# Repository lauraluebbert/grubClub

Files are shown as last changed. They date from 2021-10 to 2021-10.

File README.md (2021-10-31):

# grubClub
Please cite the information in this repository using the following DOI:  


I would like to present grubClub (“grub” for larva, and “club” for… well, you will see). I built off of the ethoscope (https://github.com/gilestrolab/ethoscope) by https://github.com/qgeissmann to enable automated long-term optogenetic stimulation of Drosophila larvae. Here is my Halloween-style release: https://twitter.com/NeuroLuebbert/status/1454220954666631170?s=20

GrubClub consists of a printed circuit board (PCB) and an accompanying arena. Both fit into the ethoscope published here: https://journals.plos.org/plosbiology/article?id=10.1371/journal.pbio.2003026.

The PCB holds 4 transistors, each connecting to 2 LEDs. Each row of LEDs can be controlled independently through Raspberry Pi GPIOs. In the picture below, each LED has a 270 ohm resistor. The power of the LEDs can be increased (or decreased) by modifying this resistance (within the circuit limits). 

The grubClub arena slides into the ethoscope and holds larvae in small round wells that can be filled with sugar-containing agar (or any larva medium). Each square fits a standard 22x22 mm coverslip as a lid. I 3D-printed my arena using translucent PLA to increase light intensity.

Since I am currently not recording larval behavior, I did not include an IR backlight for camera recordings. However, the PCB is designed such that an IR light strip can easily fit between the LED rows, enabling optogenetic stimulation and behavior recording at the same time. Finally, while red LEDs (~630 nm) might prevent a startle response, for my experimental design, I decided to stimulate at the spectral peak of my channelrhodopsin Chrimson (590 nm). The PCB supports LEDs of any color, and I included both options in the component list.

<p float="left">
  
   
</p>

<p float="left">
  
   
</p>

[grubClub PCB](https://user-images.githubusercontent.com/56094636/139601286-2ef72724-cccf-4f6b-9c9d-bd818d46505a.mp4)

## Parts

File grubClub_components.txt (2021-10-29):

2N3904 transistor:  
https://www.digikey.com/en/products/detail/nte-electronics-inc/2N3904/11648305

Yellow LEDs:  
https://www.digikey.com/en/products/detail/lumileds/LXM2-PL01-0000/3961250?s=N4IgjCBcoCwAxVAYygMwIYBsDOBTANCAPZQDaIATDAOwDMcArCIVXQGwQC6hADgC5QQAZT4AnAJYA7AOYgAvoQC0MRCBSQMOAsTIhaADgoBONiE4KQiiqvViArtpKRyRs3IvXnIUbgBGuTAACTDsAD1wiSTcgA

Red LEDs:  
https://www.digikey.com/en/products/detail/lumileds/LXM2-PD01-0050/3961247

PCB machined by https://oshpark.com/.

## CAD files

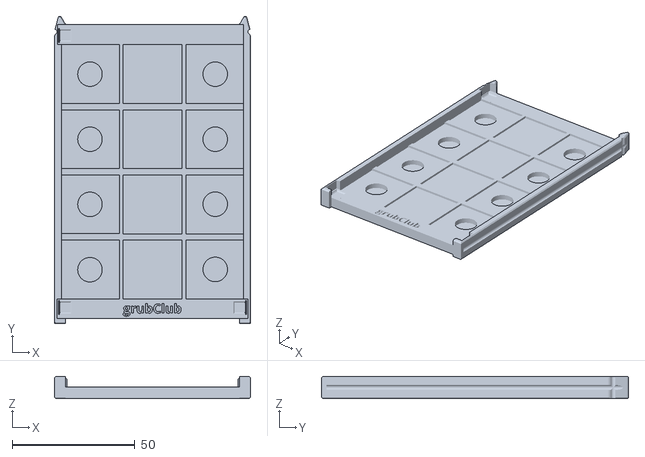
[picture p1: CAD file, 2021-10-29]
grubClub_arena_v2.stl
80.0 x 125.2 x 9.00

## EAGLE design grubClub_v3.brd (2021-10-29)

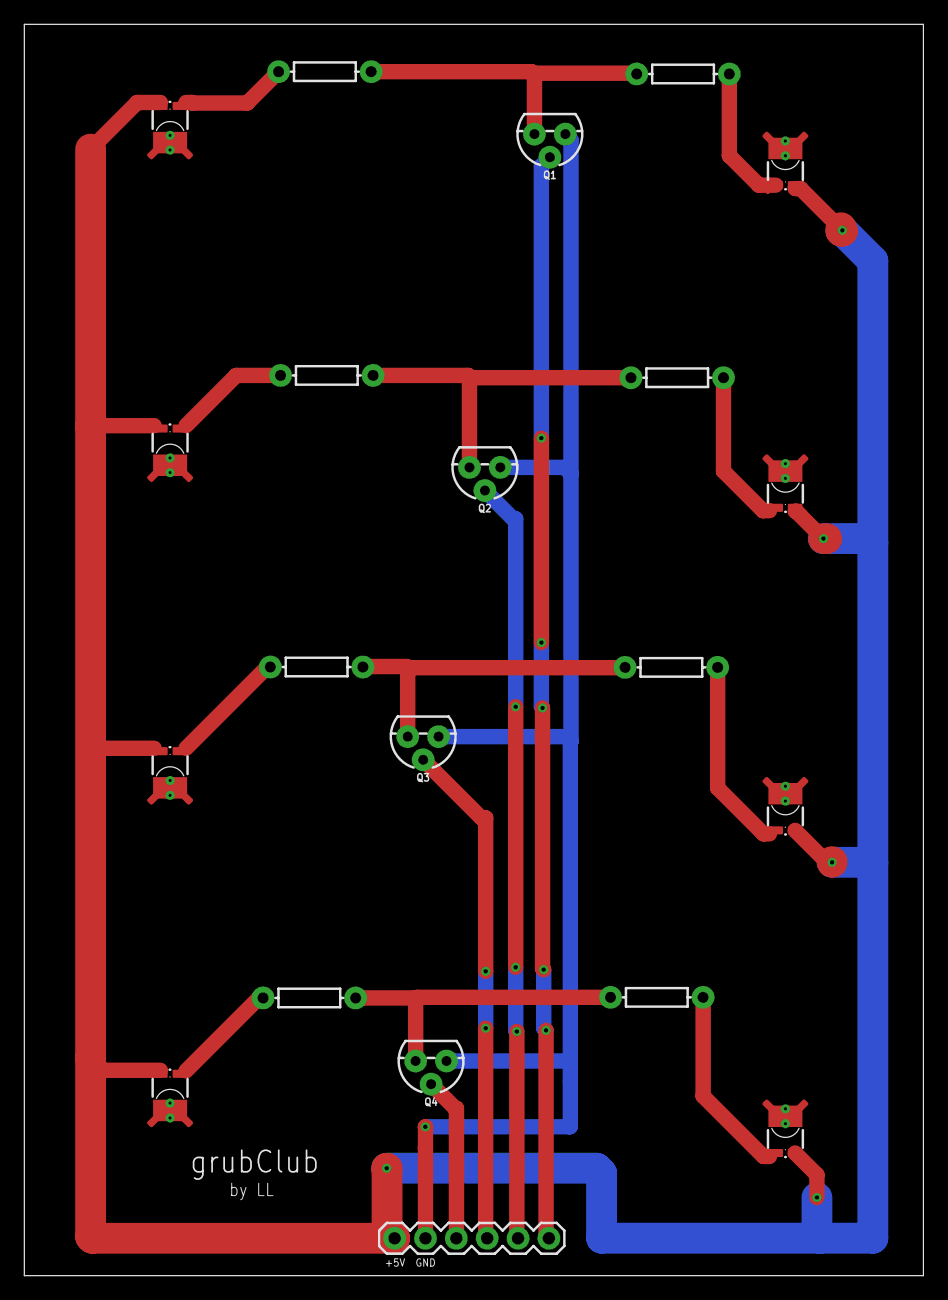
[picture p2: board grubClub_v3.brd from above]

Board: 2 copper layers, 74.0 x 103.0 mm, 21 parts (0 on the bottom side), 20 nets.

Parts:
J6: 1X06
LED1, LED2, LED3, LED4, LED5, LED6, LED7, LED8: LUXEON_REBEL
Q1, Q2, Q3, Q4: 200mA/40V; TO-92
R1, R2, R3, R4, R5, R6, R7, R8: AXIAL-0.3

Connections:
unnamed: LED7.C, LED7.C@1, R1.P$1
unnamed: J6.4, Q4.2
unnamed: J6.3, Q3.2
unnamed: J6.2, Q2.2
unnamed: J6.1, Q1.2
unnamed: LED1.C, LED1.C@1, R4.P$1
unnamed: J6.6, LED1.A, LED1.A@1, LED2.A, LED2.A@1, LED3.A, LED3.A@1, LED4.A, LED4.A@1, LED6.A, LED6.A@1, LED7.A, LED7.A@1, LED8.A, LED8.A@1
unnamed: LED3.C, LED3.C@1, R3.P$1
unnamed: LED5.C, LED5.C@1, R2.P$1
unnamed: LED8.C, LED8.C@1, R6.P$2
unnamed: LED6.C, LED6.C@1, R7.P$2
unnamed: LED4.C, LED4.C@1, R8.P$2
unnamed: LED2.C, LED2.C@1, R5.P$2
unnamed: Q1.3, R4.P$2, R5.P$1
unnamed: Q2.3, R3.P$2, R8.P$1
unnamed: Q3.3, R2.P$2, R7.P$1
unnamed: Q4.3, R1.P$2, R6.P$1
unnamed: J6.5, Q1.1, Q2.1, Q3.1, Q4.1
S$1: LED5.A, LED5.A@1
TH: LED1.TH, LED1.TH@1, LED1.TH@2, LED1.TH@3, LED1.TH@4, LED2.TH, LED2.TH@1, LED2.TH@2, LED2.TH@3, LED2.TH@4, LED3.TH, LED3.TH@1, LED3.TH@2, LED3.TH@3, LED3.TH@4, LED4.TH, LED4.TH@1, LED4.TH@2, LED4.TH@3, LED4.TH@4, LED5.TH, LED5.TH@1, LED5.TH@2, LED5.TH@3, LED5.TH@4, LED6.TH, LED6.TH@1, LED6.TH@2, LED6.TH@3, LED6.TH@4, LED7.TH, LED7.TH@1, LED7.TH@2, LED7.TH@3, LED7.TH@4, LED8.TH, LED8.TH@1, LED8.TH@2, LED8.TH@3, LED8.TH@4

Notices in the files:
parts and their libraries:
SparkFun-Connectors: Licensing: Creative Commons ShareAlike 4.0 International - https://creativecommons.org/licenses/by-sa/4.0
